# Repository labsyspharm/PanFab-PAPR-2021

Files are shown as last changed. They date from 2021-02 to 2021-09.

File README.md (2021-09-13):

# PanFab-PAPR-2021
Greater Boston Pandemic Fabrication Team Powered Air-Purifying Respirator (PanFab PAPR)

Akshay Kothakonda, Lyla Atta, Deborah Plana, Ferrous Ward, Nicole R. LeBoeuf, Peter K. Sorger, <i>et al </i>. 

Publication: https://www.frontiersin.org/articles/10.3389/fbioe.2021.690905/full

Website Intro Page Image-01

<br />This work is licensed under a <a rel="license" href="http://creativecommons.org/licenses/by-sa/4.0/">Creative Commons Attribution-ShareAlike 4.0 International License</a>.

Creative Commons License

This work is licensed under a Creative Commons Attribution-ShareAlike 4.0 International License.

Creative Commons Attribution-ShareAlike 4.0 International Public License

By exercising the Licensed Rights (defined below), You accept and agree to be bound by the terms and conditions of this Creative Commons Attribution-ShareAlike 4.0 International Public License ("Public License"). To the extent this Public License may be interpreted as a contract, You are granted the Licensed Rights in consideration of Your acceptance of these terms and conditions, and the Licensor grants You such rights in consideration of benefits the Licensor receives from making the Licensed Material available under these terms and conditions.

Section 1 – Definitions.

a.	Adapted Material means material subject to Copyright and Similar Rights that is derived from or based upon the Licensed Material and in which the Licensed Material is translated, altered, arranged, transformed, or otherwise modified in a manner requiring permission under the Copyright and Similar Rights held by the Licensor. For purposes of this Public License, where the Licensed Material is a musical work, performance, or sound recording, Adapted Material is always produced where the Licensed Material is synched in timed relation with a moving image.

b.	Adapter's License means the license You apply to Your Copyright and Similar Rights in Your contributions to Adapted Material in accordance with the terms and conditions of this Public License.

c.	BY-SA Compatible License means a license listed at creativecommons.org/compatiblelicenses, approved by Creative Commons as essentially the equivalent of this Public License.

d.	Copyright and Similar Rights means copyright and/or similar rights closely related to copyright including, without limitation, performance, broadcast, sound recording, and Sui Generis Database Rights, without regard to how the rights are labeled or categorized. For purposes of this Public License, the rights specified in Section 2(b)(1)-(2) are not Copyright and Similar Rights.

e.	Effective Technological Measures means those measures that, in the absence of proper authority, may not be circumvented under laws fulfilling obligations under Article 11 of the WIPO Copyright Treaty adopted on December 20, 1996, and/or similar international agreements.

f.	Exceptions and Limitations means fair use, fair dealing, and/or any other exception or limitation to Copyright and Similar Rights that applies to Your use of the Licensed Material.

g.	License Elements means the license attributes listed in the name of a Creative Commons Public License. The License Elements of this Public License are Attribution and ShareAlike.

h.	Licensed Material means the artistic or literary work, database, or other material to which the Licensor applied this Public License.

i.	Licensed Rights means the rights granted to You subject to the terms and conditions of this Public License, which are limited to all Copyright and Similar Rights that apply to Your use of the Licensed Material and that the Licensor has authority to license.

j.	Licensor means the individual(s) or entity(ies) granting rights under this Public License.

k.	Share means to provide material to the public by any means or process that requires permission under the Licensed Rights, such as reproduction, public display, public performance, distribution, dissemination, communication, or importation, and to make material available to the public including in ways that members of the public may access the material from a place and at a time individually chosen by them.

l.	Sui Generis Database Rights means rights other than copyright resulting from Directive 96/9/EC of the European Parliament and of the Council of 11 March 1996 on the legal protection of databases, as amended and/or succeeded, as well as other essentially equivalent rights anywhere in the world.

m.	You means the individual or entity exercising the Licensed Rights under this Public License. Your has a corresponding meaning.
Section 2 – Scope.

a.	License grant. 

1.	Subject to the terms and conditions of this Public License, the Licensor hereby grants You a worldwide, royalty-free, non-sublicensable, non-exclusive, irrevocable license to exercise the Licensed Rights in the Licensed Material to: 

A.	reproduce and Share the Licensed Material, in whole or in part; and

B.	produce, reproduce, and Share Adapted Material.

2.	Exceptions and Limitations. For the avoidance of doubt, where Exceptions and Limitations apply to Your use, this Public License does not apply, and You do not need to comply with its terms and conditions.

3.	Term. The term of this Public License is specified in Section 6(a).

4.	Media and formats; technical modifications allowed. The Licensor authorizes You to exercise the Licensed Rights in all media and formats whether now known or hereafter created, and to make technical modifications necessary to do so. The Licensor waives and/or agrees not to assert any right or authority to forbid You from making technical modifications necessary to exercise the Licensed Rights, including technical modifications necessary to circumvent Effective Technological Measures. For purposes of this Public License, simply making modifications authorized by this Section 2(a)(4) never produces Adapted Material.

5.	Downstream recipients. 

A.	Offer from the Licensor – Licensed Material. Every recipient of the Licensed Material automatically receives an offer from the Licensor to exercise the Licensed Rights under the terms and conditions of this Public License.

B.	Additional offer from the Licensor – Adapted Material. Every recipient of Adapted Material from You automatically receives an offer from the Licensor to exercise the Licensed Rights in the Adapted Material under the conditions of the Adapter’s License You apply.

C.	No downstream restrictions. You may not offer or impose any additional or different terms or conditions on, or apply any Effective Technological Measures to, the Licensed Material if doing so restricts exercise of the Licensed Rights by any recipient of the Licensed Material.

6.	No endorsement. Nothing in this Public License constitutes or may be construed as permission to assert or imply that You are, or that Your use of the Licensed Material is, connected with, or sponsored, endorsed, or granted official status by, the Licensor or others designated to receive attribution as provided in Section 3(a)(1)(A)(i).

b.	Other rights.

1.	Moral rights, such as the right of integrity, are not licensed under this Public License, nor are publicity, privacy, and/or other similar personality rights; however, to the extent possible, the Licensor waives and/or agrees not to assert any such rights held by the Licensor to the limited extent necessary to allow You to exercise the Licensed Rights, but not otherwise.

2.	Patent and trademark rights are not licensed under this Public License.

3.	To the extent possible, the Licensor waives any right to collect royalties from You for the exercise of the Licensed Rights, whether directly or through a collecting society under any voluntary or waivable statutory or compulsory licensing scheme. In all other cases the Licensor expressly reserves any right to collect such royalties.

Section 3 – License Conditions.

Your exercise of the Licensed Rights is expressly made subject to the following conditions.

a.	Attribution.

1.	If You Share the Licensed Material (including in modified form), You must:

A.	retain the following if it is supplied by the Licensor with the Licensed Material: 

i.	identification of the creator(s) of the Licensed Material and any others designated to receive attribution, in any reasonable manner requested by the Licensor (including by pseudonym if designated);

ii.	a copyright notice;

iii.	a notice that refers to this Public License; 

iv.	a notice that refers to the disclaimer of warranties;

v.	a URI or hyperlink to the Licensed Material to the extent reasonably practicable;

B.	indicate if You modified the Licensed Material and retain an indication of any previous modifications; and

C.	indicate the Licensed Material is licensed under this Public License, and include the text of, or the URI or hyperlink to, this Public License.

2.	You may satisfy the conditions in Section 3(a)(1) in any reasonable manner based on the medium, means, and context in which You Share the Licensed Material. For example, it may be reasonable to satisfy the conditions by providing a URI or hyperlink to a resource that includes the required information.

3.	If requested by the Licensor, You must remove any of the information required by Section 3(a)(1)(A) to the extent reasonably practicable.

b.	ShareAlike. 

In addition to the conditions in Section 3(a), if You Share Adapted Material You produce, the following conditions also apply.

1.	The Adapter’s License You apply must be a Creative Commons license with the same License Elements, this version or later, or a BY-SA Compatible License.

2.	You must include the text of, or the URI or hyperlink to, the Adapter's License You apply. You may satisfy this condition in any reasonable manner based on the medium, means, and context in which You Share Adapted Material.

3.	You may not offer or impose any additional or different terms or conditions on, or apply any Effective Technological Measures to, Adapted Material that restrict exercise of the rights granted under the Adapter's License You apply.

Section 4 – Sui Generis Database Rights.

Where the Licensed Rights include Sui Generis Database Rights that apply to Your use of the Licensed Material:

a.	for the avoidance of doubt, Section 2(a)(1) grants You the right to extract, reuse, reproduce, and Share all or a substantial portion of the contents of the database;

b.	if You include all or a substantial portion of the database contents in a database in which You have Sui Generis Database Rights, then the database in which You have Sui Generis Database Rights (but not its individual contents) is Adapted Material, including for purposes of Section 3(b); and

c.	You must comply with the conditions in Section 3(a) if You Share all or a substantial portion of the contents of the database.

For the avoidance of doubt, this Section 4 supplements and does not replace Your obligations under this Public License where the Licensed Rights include other Copyright and Similar Rights. 

Section 5 – Disclaimer of Warranties and Limitation of Liability.

a.	Unless otherwise separately undertaken by the Licensor, to the extent possible, the Licensor offers the Licensed Material as-is and as-available, and makes no representations or warranties of any kind concerning the Licensed Material, whether express, implied, statutory, or other. This includes, without limitation, warranties of title, merchantability, fitness for a particular purpose, non-infringement, absence of latent or other defects, accuracy, or the presence or absence of errors, whether or not known or discoverable. Where disclaimers of warranties are not allowed in full or in part, this disclaimer may not apply to You.

b.	To the extent possible, in no event will the Licensor be liable to You on any legal theory (including, without limitation, negligence) or otherwise for any direct, special, indirect, incidental, consequential, punitive, exemplary, or other losses, costs, expenses, or damages arising out of this Public License or use of the Licensed Material, even if the Licensor has been advised of the possibility of such losses, costs, expenses, or damages. Where a limitation of liability is not allowed in full or in part, this limitation may not apply to You.

c.	The disclaimer of warranties and limitation of liability provided above shall be interpreted in a manner that, to the extent possible, most closely approximates an absolute disclaimer and waiver of all liability.

Section 6 – Term and Termination.

a.	This Public License applies for the term of the Copyright and Similar Rights licensed here. However, if You fail to comply with this Public License, then Your rights under this Public License terminate automatically.

b.	Where Your right to use the Licensed Material has terminated under Section 6(a), it reinstates:

1.	automatically as of the date the violation is cured, provided it is cured within 30 days of Your discovery of the violation; or

2.	upon express reinstatement by the Licensor.

For the avoidance of doubt, this Section 6(b) does not affect any right the Licensor may have to seek remedies for Your violations of this Public License.

c.	For the avoidance of doubt, the Licensor may also offer the Licensed Material under separate terms or conditions or stop distributing the Licensed Material at any time; however, doing so will not terminate this Public License.

d.	Sections 1, 5, 6, 7, and 8 survive termination of this Public License.

Section 7 – Other Terms and Conditions.

a.	The Licensor shall not be bound by any additional or different terms or conditions communicated by You unless expressly agreed.

b.	Any arrangements, understandings, or agreements regarding the Licensed Material not stated herein are separate from and independent of the terms and conditions of this Public License.

Section 8 – Interpretation.

a.	For the avoidance of doubt, this Public License does not, and shall not be interpreted to, reduce, limit, restrict, or impose conditions on any use of the Licensed Material that could lawfully be made without permission under this Public License.

b.	To the extent possible, if any provision of this Public License is deemed unenforceable, it shall be automatically reformed to the minimum extent necessary to make it enforceable. If the provision cannot be reformed, it shall be severed from this Public License without affecting the enforceability of the remaining terms and conditions.

c.	No term or condition of this Public License will be waived and no failure to comply consented to unless expressly agreed to by the Licensor.

d.	Nothing in this Public License constitutes or may be interpreted as a limitation upon, or waiver of, any privileges and immunities that apply to the Licensor or You, including from the legal processes of any jurisdiction or authority.

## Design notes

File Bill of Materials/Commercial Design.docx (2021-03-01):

Bill of Materials for PanFab Commercial PAPR Design

Akshay Kothakonda¹ ,², *, Lyla Atta¹,³, *, Deborah Plana¹ ,⁴,⁵, *, Ferrous Ward¹ ,², *, Chris Davis¹,⁶, Avilash Cramer¹ ,⁵, Robert Moran¹ ,⁷, Jacob Freake¹,⁸, Enze Tian¹,⁹, Ofer Mazor¹,¹⁰, Pavel Gorelik¹,¹⁰, Christopher Van¹,¹¹, Christopher Hansen¹,¹², Helen Yang¹,¹³, Michael S. Sinha¹,¹³, Ju Li¹,¹⁴, Sherry H. Yu¹,¹⁵, Nicole R. LeBoeuf1,16, †, Peter K. Sorger1,4, †

¹ Greater Boston Pandemic Fabrication Team (PanFab) c/o Harvard-MIT Center for Regulatory Science, Harvard Medical School, Boston, MA, USA

²Department of Aeronautics and Astronautics, MIT, Cambridge, MA, USA

³Johns Hopkins University School of Medicine, Baltimore, MD, USA

⁴Harvard Ludwig Cancer Research Center and Department of Systems Biology, Harvard Medical School, Boston, MA, USA

⁵ Harvard-MIT Division of Health Sciences & Technology, Cambridge, MA, USA

⁶GenOne Technologies, Cambridge, MA, USA

⁷Mine Survival, Panama City Beach, FL, USA

⁸Fikst Product Development, Woburn, MA, USA

⁹Beijing Key Laboratory of Indoor Air Quality Evaluation and Control, Department of Building Science, Tsinghua University, Beijing, China

¹⁰Research Instrumentation Core Facility, Harvard Medical School, Boston, MA, USA

¹¹Borobot, Middleborough, MA, USA

¹²Harvard Graduate School of Design, Cambridge, MA, USA

¹³Harvard-MIT Center for Regulatory Science, Harvard Medical School, Boston MA, USA

¹⁴Department of Nuclear Science and Engineering and Department of Materials Science and Engineering, MIT, Cambridge, MA, USA

¹⁵Department of Dermatology, Yale School of Medicine, New Haven, CT USA

¹⁶ Department of Dermatology, Center for Cutaneous Oncology, Brigham and Women’s Hospital and Dana-Farber Cancer Institute, Boston, MA, USA

*These authors contributed equally to this work

†Co-corresponding authors. E-mails: nleboeuf@bwh.harvard.edu; peter_sorger@hms.harvard.edu cc: Maureen_Bergeron@hms.harvard.edu;

ORCID IDs:

Akshay Kothakonda, 0000-0001-5424-4228

Lyla Atta, 0000-0002-6113-0082

Deborah Plana, 0000-0002-4218-1693

Avilash Cramer, 0000-0003-0014-8921

Jacob Freake, 0000-0002-5198-835X

Enze Tian, 0000-0001-6410-5360

Christopher Van, 0000-0003-3262-964X

Christopher Hansen, 0000-0002-6640-2745

Ju Li, PhD, 0000-0002-7841-8058

Helen Yang, 0000-0002-9455-5300

Michael S. Sinha 0000-0002-9165-8611

Sherry H. Yu: 0000-0002-1432-9128

Nicole R. LeBoeuf, MD, MPH, 0000-0002-8264-834X

Peter Sorger, PhD, 0000-0002-3364-1838

Following are the parts used in the PanFab Commercial PAPR Design. The estimated costs assume a total production run of 2000 units.

S. No. | Item | Qty. | Supplier/Method | Part No. | Estimated cost ($)
1 | Enclosure | 1 | Pelican | V100 Vault | 40
2 | Threaded Inserts for Filter | 2 | ABS Molding | N/A | 6 (Tooling Cost = 6645)
3 | Threaded Insert for Hose | 1 | ABS Molding | N/A | 2.80 (Tooling Cost = 6846)
4 | Blower, Centrifugal | 1 | Delta Electronics | BFB1012HD-04D4L | 36
5 | Battery pack, 12V NiMH | 1 | Tenergy | Amazon Standard Identification Number: B077Y9HNTF | 23
6 | Controller | 1 | Arduino | R3 | 23
7 | PCB Shield | 1 | OSH Park | N/A | 9.50
8 | Differential Pressure Sensor | 1 | Sensirion | SDP810-500PA | 19
9 | Buzzer | 1 | Mallory Sonalert Products | PS-580Q | 5
10 | Potentiometer | 1 | Bourns Inc. | 93R1A-R22-A12L | 3
11 | Transistor | 1 | ON Semiconductor | 2N3904BU | 0.20
12 | Resistor | 1 | Vishay BC Semiconductor | PR02000201001JR500 | 0.32
13 | Electrical connector | 1 | TE Connectivity AMP Connectors | 1-2834184-3 | 1.40
14 | Venturi | 1 | BPE Inc. | 178-71-2 | 0.54
15 | Venturi Ports | 2 | Car-Anth Manufacturing | 16-1204-2 | 0.68 (Tooling Cost = 375)
16 | Blower silicone tube | 1 | McMaster-Carr | 3038K29 | N/A
17 | Venturi silicone tube | 2 | McMaster-Carr | 3038K12 | N/A
18 | Blower adapter | 1 | ABS 3D printing | N/A | 6
20 | Switch | 1 | McMaster-Carr | 8002K114 | 28
21 | Switch Cover | 1 | McMaster-Carr | 70205K4 | 4.40
22 | Gaskets for threaded connections | 4 | McMaster-Carr | 5647K62 | 3
23 | Waist strap | 1 | Skil-Care | PathoShield Gait Belt | 11
24 | Filter | 2 | Milwaukee | 49-90-1900 | 40
25 | Filter Adapter | 2 | ABS Injection molding | N/A | 6 (Tooling Cost = 6846)
26 | Filter Cover | 2 | ABS Injection molding | N/A | 8 (Tooling Cost = 18345)
27 | Hose adapter | 2 | ABS Injection molding | N/A | 6.60 (Tooling Cost = 9997)
28 | Hose | 1 | Flexaust | Flex-Tube PU-IH, PN: 33800125000 | 8.50
29 | Hood coupler | 1 | ABS Injection molding | N/A | 3.30 (Tooling Cost = 7456)
30 | Locking ring | 1 | ABS Injection molding | N/A | 2.70 (Tooling Cost = 5156)
31 | Hood | 1 | University of Washington | VHA ADAPT PAPR Hood | 30
Total | | | | | 327.94

Notes:

1. Several costs are unofficial quotes

2. Tooling cost for machining the Pelican case and joining the threaded inserts (Items 2 and 3) are TBD

© President and Fellows of Harvard College and The Massachusetts Institute of Technology, 2020.

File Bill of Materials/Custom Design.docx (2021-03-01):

Bill of Materials for PanFab Custom PAPR Design

Akshay Kothakonda¹ ,², *, Lyla Atta¹,³, *, Deborah Plana¹ ,⁴,⁵, *, Ferrous Ward¹ ,², *, Chris Davis¹,⁶, Avilash Cramer¹ ,⁵, Robert Moran¹ ,⁷, Jacob Freake¹,⁸, Enze Tian¹,⁹, Ofer Mazor¹,¹⁰, Pavel Gorelik¹,¹⁰, Christopher Van¹,¹¹, Christopher Hansen¹,¹², Helen Yang¹,¹³, Michael S. Sinha¹,¹³, Ju Li¹,¹⁴, Sherry H. Yu¹,¹⁵, Nicole R. LeBoeuf1,16, †, Peter K. Sorger1,4, †

¹ Greater Boston Pandemic Fabrication Team (PanFab) c/o Harvard-MIT Center for Regulatory Science, Harvard Medical School, Boston, MA, USA

²Department of Aeronautics and Astronautics, MIT, Cambridge, MA, USA

³Johns Hopkins University School of Medicine, Baltimore, MD, USA

⁴Harvard Ludwig Cancer Research Center and Department of Systems Biology, Harvard Medical School, Boston, MA, USA

⁵ Harvard-MIT Division of Health Sciences & Technology, Cambridge, MA, USA

⁶GenOne Technologies, Cambridge, MA, USA

⁷Mine Survival, Panama City Beach, FL, USA

⁸Fikst Product Development, Woburn, MA, USA

⁹Beijing Key Laboratory of Indoor Air Quality Evaluation and Control, Department of Building Science, Tsinghua University, Beijing, China

¹⁰Research Instrumentation Core Facility, Harvard Medical School, Boston, MA, USA

¹¹Borobot, Middleborough, MA, USA

¹²Harvard Graduate School of Design, Cambridge, MA, USA

¹³Harvard-MIT Center for Regulatory Science, Harvard Medical School, Boston MA, USA

¹⁴Department of Nuclear Science and Engineering and Department of Materials Science and Engineering, MIT, Cambridge, MA, USA

¹⁵Department of Dermatology, Yale School of Medicine, New Haven, CT USA

¹⁶ Department of Dermatology, Center for Cutaneous Oncology, Brigham and Women’s Hospital and Dana-Farber Cancer Institute, Boston, MA, USA

*These authors contributed equally to this work

†Co-corresponding authors. E-mails: nleboeuf@bwh.harvard.edu; peter_sorger@hms.harvard.edu cc: Maureen_Bergeron@hms.harvard.edu;

ORCID IDs:

Akshay Kothakonda, 0000-0001-5424-4228

Lyla Atta, 0000-0002-6113-0082

Deborah Plana, 0000-0002-4218-1693

Avilash Cramer, 0000-0003-0014-8921

Jacob Freake, 0000-0002-5198-835X

Enze Tian, 0000-0001-6410-5360

Christopher Van, 0000-0003-3262-964X

Christopher Hansen, 0000-0002-6640-2745

Ju Li, PhD, 0000-0002-7841-8058

Helen Yang, 0000-0002-9455-5300

Michael S. Sinha 0000-0002-9165-8611

Sherry H. Yu: 0000-0002-1432-9128

Nicole R. LeBoeuf, MD, MPH, 0000-0002-8264-834X

Peter Sorger, PhD, 0000-0002-3364-1838

Following are the parts used in the PanFab Custom PAPR Design. The estimated costs assume a total production run of 2000 units.

S. No. | Item | Qty. | Supplier/Method | Part No. | Estimated cost ($)
1 | Housing Bin | 1 | ABS Injection Molding | N/A | 9.60 (Tooling Cost = 10,720)
2 | Housing Lid | 1 | ABS Injection Molding | N/A | 9.70 (Tooling Cost = 19,589)
3 | Blower, Centrifugal | 1 | Delta Electronics | BFB1012HD-04D4L | 36
4 | Battery pack, 12V NiMH | 1 | Tenergy | Amazon Standard Identification Number: B077Y9HNTF | 23
5 | Controller | 1 | Arduino | R3 | 23
6 | PCB Shield | 1 | OSH Park | N/A | 9.50
7 | Differential Pressure Sensor | 1 | Sensirion | SDP810-500PA | 19
8 | Buzzer | 1 | Mallory Sonalert Products | PS-580Q | 5
9 | Potentiometer | 1 | Bourns Inc. | 93R1A-R22-A12L | 3
10 | Transistor | 1 | ON Semiconductor | 2N3904BU | 0.20
11 | Resistor | 1 | Vishay BC Semiconductor | PR02000201001JR500 | 0.32
12 | Electrical connector | 1 | TE Connectivity AMP Connectors | 1-2834184-3 | 1.40
13 | Venturi | 1 | BPE Inc. | 178-71-2 | 0.54
14 | Venturi Ports | 2 | Car-Anth Manufacturing | 16-1204-2 | 0.68 (Tooling Cost = 375)
15 | Blower silicone tube | 1 | McMaster-Carr | 3038K29 | N/A
16 | Venturi silicone tube | 2 | McMaster-Carr | 3038K12 | N/A
17 | Blower adapter | 1 | ABS 3D printing | N/A | 6
18 | Housing Gasket | 1 | Apple Rubber | N/A | 3.20 (Tooling Cost = 2560)
19 | Housing Latches | 4 | McMaster-Carr | 1794A55 | 15.20
20 | Gaskets for threaded connections | 4 | McMaster-Carr | 5647K62 | 3
21 | Latch screws | 16 | McMaster-Carr | 98164A441 | 1.55
22 | Latch nuts | 16 | McMaster-Carr | 90730A007 | 0.65
23 | Switch | 1 | McMaster-Carr | 8002K114 | 28
24 | Switch Cover | 1 | McMaster-Carr | 70205K4 | 4.40
25 | Waist strap | 1 | Skil-Care | PathoShield Gait Belt | 11
26 | Filter | 2 | Custom Filters | N/A | 19 (Tooling Cost = 26020)
27 | Hose adapter | 2 | ABS Injection molding | N/A | 6.60 (Tooling Cost = 9997)
28 | Hose | 1 | Flexaust | Flex-Tube PU-IH, PN: 33800125000 | 8.50
29 | Hood coupler | 1 | ABS Injection molding | N/A | 3.30 (Tooling Cost = 7456)
30 | Locking ring | 1 | ABS Injection molding | N/A | 2.70 (Tooling Cost = 5156)
31 | Hood | 1 | University of Washington | VHA ADAPT PAPR Hood | 30
Total | | | | | 284.04

Note: Several costs are unofficial quotes

© President and Fellows of Harvard College and The Massachusetts Institute of Technology, 2020.

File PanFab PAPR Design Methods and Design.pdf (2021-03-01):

© President and Fellows of Harvard College and The Massachusetts Institute of Technology,

PanFab PAPR Design Methods and Design
Akshay Kothakonda¹ ,2, *, Lyla Atta¹,3, *, Deborah Plana¹ ,4,5, *, Ferrous Ward¹ ,2, *, Chris Davis¹,6, Avilash Cramer¹ ,5, Robert Moran¹ ,7, Jacob Freake¹,8, Enze Tian¹,9, Ofer Mazor¹,10, Pavel Gorelik¹,10, Christopher Van¹,11, Christopher Hansen¹,12, Helen Yang¹,13, Michael S. Sinha¹,13, Ju Li¹,14, Sherry H. Yu¹,15, Nicole R. LeBoeuf¹,16, †, Peter K. Sorger¹,4, †
1 Greater Boston Pandemic Fabrication Team (PanFab) c/o Harvard-MIT Center for Regulatory Science, Harvard Medical School, Boston, MA, USA
2
Department of Aeronautics and Astronautics, MIT, Cambridge, MA, USA
3
Johns Hopkins University School of Medicine, Baltimore, MD, USA
4
Harvard Ludwig Cancer Research Center and Department of Systems Biology, Harvard Medical School, Boston, MA, USA
5 Harvard-MIT Division of Health Sciences & Technology, Cambridge, MA, USA
6
GenOne Technologies, Cambridge, MA, USA
7
Mine Survival, Panama City Beach, FL, USA
8
Fikst Product Development, Woburn, MA, USA
9
Beijing Key Laboratory of Indoor Air Quality Evaluation and Control, Department of Building Science, Tsinghua University, Beijing, China
10Research Instrumentation Core Facility, Harvard Medical School, Boston, MA, USA 11Borobot, Middleborough, MA, USA
12Harvard Graduate School of Design, Cambridge, MA, USA
13Harvard-MIT Center for Regulatory Science, Harvard Medical School, Boston MA, USA 14Department of Nuclear Science and Engineering and Department of Materials Science and Engineering, MIT, Cambridge, MA, USA
15Department of Dermatology, Yale School of Medicine, New Haven, CT USA
16 Department of Dermatology, Center for Cutaneous Oncology, Brigham and Women’s Hospital and Dana-Farber Cancer Institute, Boston, MA, USA

*
These authors contributed equally to this work
†
Co-corresponding authors. E-mails: nleboeuf@bwh.harvard.edu; peter_sorger@hms.harvard.edu cc: Maureen_Bergeron@hms.harvard.edu;

ORCID IDs:
Akshay Kothakonda, 0000-0001-5424-4228
Lyla Atta, 0000-0002-6113-0082
Deborah Plana, 0000-0002-4218-1693 Avilash Cramer, 0000-0003-0014-8921 Jacob Freake, 0000-0002-5198-835X Enze Tian, 0000-0001-6410-5360 Christopher Van, 0000-0003-3262-964X Christopher Hansen, 0000-0002-6640-2745 Ju Li, PhD, 0000-0002-7841-8058

© President and Fellows of Harvard College and The Massachusetts Institute of Technology,

Helen Yang, 0000-0002-9455-5300
Michael S. Sinha 0000-0002-9165-8611
Sherry H. Yu: 0000-0002-1432-9128
Nicole R. LeBoeuf, MD, MPH, 0000-0002-8264-834X Peter Sorger, PhD, 0000-0002-3364-1838

METHODS
This section describes the methodology pursued in designing the PanFab Custom PAPR and PanFab Commercial PAPR filters and blower units.
Filter selection
NIOSH regulations designate several classes of PAPRs depending on filtration requirements. A key distinction between classes is whether the respirator is approved for use with oil-based aerosols (P type filters, tested for filtration efficiency with dioctyl phthalate (DOP)) or only aqueous aerosols (N type filters, tested for filtration efficiency with NaCl-containing droplets). Commercial PAPR filter cartridges are commonly of the P100 type as they provide protection against both oil and salt-based aqueous aerosols. Another, less commonly used, class of PAPR filter is the N100, which only needs to demonstrate its effectiveness against salt-based aqueous aerosols and not oil. Here, “100” after the type designation refers to filters demonstrating filtration of 99.97% of tested particles¹.
The pressure drop across a filter at the required airflow is an additional consideration that affects blower selection and power consumption. The pressure drop should be as low as possible for a given filtration efficiency, so as to permit the use of a less powerful blower, and consequently a smaller battery, making the system lighter and able to operate longer between charging².

© President and Fellows of Harvard College and The Massachusetts Institute of Technology,

In selecting the PanFab Commercial Filter Cartridge, our goal was to identify and test commercially available products whose supply would not be impacted by shortages during pandemic conditions, and which would be easily adaptable to various blower units. The PanFab Custom Filter Cartridge was designed to have a small overall volume, be lightweight, and have integrated connection features to allow for compatibility with various blower units.

Blower Unit Design

The PAPR blower units consist of a blower, battery, buzzer to warn of low flow rate, control systems, and a housing to enclose these components. The PanFab commercial and custom units were designed to be comfortable to wear for extended periods of time, to be easy to don and doff, and to not hamper the range of motion required in clinical tasks. Additionally, the materials for the external surfaces of the unit were selected so as to be compatible with sterilization with alcohol based wipes. Below we outline the selection criteria used for each of the blower unit components.
The PanFab blowers were selected to produce enough static pressure as to overcome the pressure drop incurred from passing air through the filters and the facepiece at the required flow rate of 170 liters per minute³. The commercial and custom battery that powers the blower unit were selected to match the voltage rating of the blower and have sufficient discharge current. We also ensured the batteries had the charge capacity necessary to continuously power the blower for one hour or longer at the required flow rate, a time selected based on the recommendations from HCWs at a major academic medical center. Finally, we ensured that the blower and battery combinations met the NIOSH specification for a noise level at the user’s ears below 80 dBA³. The blower unit control system was designed to measure the air flow rate through the PAPR and to sound an alarm at a sound level above 80 dBA at the ears (as per NIOSH STP

© President and Fellows of Harvard College and The Massachusetts Institute of Technology,

CVB-APR-STP-008) to alert the wearer of a low flow condition. The control system was also designed so as to allow for modulating flow rate as needed by the wearer.
The blower unit housings were selected to couple and decouple with the filters and hose by hand without requiring specialized tools, and to be conducive to frequent opening and closing for operations including battery charging, flow rate adjustment, and troubleshooting. Since the air inside the housing has been filtered and there is negative pressure inside the housing, it is essential for the connections of the housing with the filters and the hose, as well the interface between the separable sections of the housing, to be airtight.
Facepiece selection
We used a loose-fitting facepiece, known as the VHA ADAPT PAPR Hood, developed by the The Center for Limb Loss and MoBility (CLiMB) at the University of Washington⁴. This low cost facepiece was developed as part of COVID-19 response efforts and was chosen for prototype testing as commercial facepieces were not readily available.

RESULTING DESIGNS
This section details the designs that resulted for both the PanFab Custom PAPR and the PanFab Commercial PAPR filter and blower units.

PanFab filter cartridges
PanFab Commercial Filter Cartridge
We investigated commercial High Efficiency Particulate Air (HEPA) filters commonly used in vacuum cleaners as possible candidates. HEPA filters are rated as 99.97% efficient at

© President and Fellows of Harvard College and The Massachusetts Institute of Technology,

300um particle size⁵. The cost and availability of the Milwaukee Tool (Brookfield, WI)⁶ in commercial stores was particularly well suited to the crisis-setting PanFab PAPR design.
In order to connect the Milwaukee filter to the housings, an adapter was designed, which could be either 3D printed or injection molded. This adapter would be sealed to the filter outlet on one side using sealants or adhesives such as cyanoacrylate or epoxies, and on the other side would connect to the housing using male NATO 40mm threads. Filter covers were also designed for these filter cartridges, that protect the filter sheet from damage. These covers are also designed to be printed or molded.

PanFab Custom Filter Cartridge
We also designed a custom filter cartridge in collaboration with Custom Filters LLC (Aurora, IL) to decrease the weight and size of these devices as compared to the Milwaukee filters, making them more comfortable and easier to use for prolonged periods of time in healthcare settings. These cartridges do not need a separate filter cover, since the cartridge body is designed to envelop the filter media. Additionally, Custom Filters tests every filter cartridges’ instantaneous filtration efficiency with PAO aerosol, ensuring the integrity of all filters. This filter also connects to the housing through integrated male NATO 40mm threads.

PanFab blower units
We designed the PanFab Commercial and Custom blower units to have the same internal components, with different housings enclosing the components. NIOSH guidelines specify that airflow into a loose-fitting facepiece must exceed 170 liters/minute (lpm) to ensure maintenance of positive pressure at all activity levels ⁷. We chose to design our PAPR to provide 230 lpm,

© President and Fellows of Harvard College and The Massachusetts Institute of Technology, similar to some of the commercial PAPR’s. In selecting a blower, we determined that compact centrifugal blowers (compared to axial fans) could provide the necessary static pressures needed to overcome the pressure drop created by the filter at the required flow rate, as well as to overcome losses over the flow path to the facepiece. The pressure drop across the filters at the required flow rate was determined as part of the filtration efficiency tests. The blower selected (Delta Electronics, Neihu, Taiwan, Part Number BFB1012HD-04D4L) has a maximum static pressure of 40.6 mm of H2O and a maximum flow rate of 18.3 cubic feet per meter (cfm). Additionally, the noise level generated by running the PAPR should not exceed 80 dBA per NIOSH guidelines and should allow for sufficient communication between users⁸. The blower selected has a maximum noise level rated at 50.5dBA at a distance of 1 m. In order to meet the requirements of the blower, a 12V NiMH battery pack (Tenergy, Fremont, CA, Amazon Standard Identification Number: B077Y9HNTF) was selected. The battery has a charge capacity of 2000mA, which provides almost 4 hours of continuous operation, at the maximum flow rate, which is higher than the 1hour requirement. The battery connects to the switch through a manual disconnect, which can be disconnected to connect to a Tenergy battery charger (Amazon Standard Identification Number: B08J4H39JV).
The control system of the PAPR consists of an Arduino Uno R3 (Arduino LLC, Boston, MA) board, a linear potentiometer (Precision Electronics Corporation, North York, ON, Canada, part number RV4NAYSD103A) which controls the duty cycle, and consequently the speed of the blower, a printed circuit board (PCB)-mounted, I2C protocol operated differential pressure sensor (Sensirion AG, Staefa, Switzerland, part number SDP810-500PA) which estimates the flow rate, a piezoelectric buzzer (Mallory Sonalert Products Inc., Indianapolis, IN, part number PS-580Q) which warns of low flow rate, and a manual SPST switch (purchased from McMaster-

© President and Fellows of Harvard College and The Massachusetts Institute of Technology,

Carr, Elmhurst, IL, part number 8002K114) to turn on and off the device. A custom shield was designed and printed at OSH Park (Portland, OR), which assembles with the Arduino, and solders to the various components. An Arduino Protoshield can also be used in place of the custom printed shield.
NIOSH requires PAPRs to have a low flow rate alarm that is activated when airflow into the facepiece falls below the threshold of 170 lpm, which in our design is activated below 230 lpm. In the PanFab PAPR design, the differential pressure sensor detects pressure differential across a venturi (provided by Hunter Engineering Company, Bridgeton, MO), connected to the outlet of the blower, via a 3D printed blower adapter and a 1” OD Silicone tube (purchased from McMaster-Carr, part number 3038K29). Ports of the venturi are connected to the corresponding ones on the differential pressure sensor through a 7/32” OD Silicone tube (purchased from McMaster-Carr, part number 3038K12). It should be noted that the blower adapter connecting the blower outlet to the 1” Silicone tube was designed specifically for the blower selected; a different blower would require a blower adapter design compliant with its outlet geometry. In order to calibrate the threshold differential pressure corresponding to the threshold flow rate of 230 lpm, the outlet of the venturi was first connected to the Vernier anemometer. The differential pressure sensor was connected to an Arduino Uno R3 board through a custom printed shield, compatible with the Arduino board. The differential pressure across the venturi is read on the Arduino Serial Monitor User Interface, which is plotted against the air speed as the blower speed is increased. The minimum flow rate of 230 lpm is now correlated to the corresponding differential pressure. Once this calibration is done, the differential pressure value obtained is used in microcontroller logic to sound a piezoelectric buzzer, when the differential pressure falls below this value (and the corresponding flow rate) for 10 consecutive seconds. The

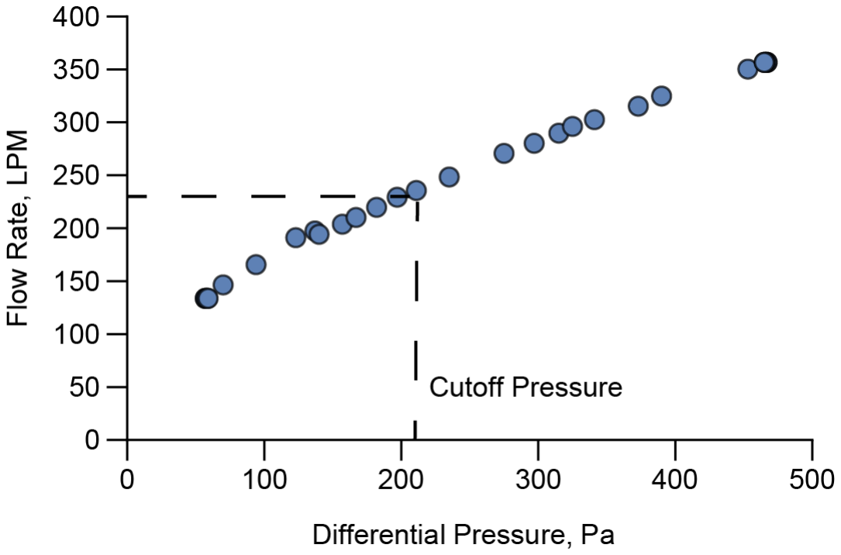
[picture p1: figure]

© President and Fellows of Harvard College and The Massachusetts Institute of Technology, plot of flow rate vs. differential pressure measured, with observed datapoints is shown in Figure 1 below. The cutoff pressure corresponding to the cutoff flow rate of 230 lpm is marked, which was programmed in the Arduino.

Figure 1: Calibration of flow rate through the venturi to the pressure differential across the device, allowing identification of cutoff pressure corresponding to the cutoff flow rate of 230 LPM. Below this cutoff pressure, the piezoelectric buzzer is programmed to sound, alerting the wearer of low flow.
The sound level of the piezoelectric buzzer needs to be loud enough so as to sufficiently alert the wearer of a low flow condition. NIOSH requires the alarm to have a sound level above 80dBA at the ears. We chose a buzzer with a higher sound level since the buzzer is placed inside the housing. Unobstructed, the buzzer chosen is specified as producing 100 dB at a distance of 100 cm.

© President and Fellows of Harvard College and The Massachusetts Institute of Technology,

In order to maximize the sound level at the ears, the piezoelectric buzzer, installed inside the housing, with filters, hose, and facepiece connected, was programmed to sound at various frequencies. The frequency producing the maximum sound level at the ears was selected, which was done for both housing types, given the different sound attenuating properties expected from the two housings. For the custom housing that will be discussed later, the frequency obtained was 500 Hz, while for the commercial housing, it was 1500 Hz.
In order to simplify the control electronic design and code, a compensatory logic that would automatically increase the flow rate in the event of flow obstruction was considered but not adopted. Based on clinical feedback, very few scenarios were known to exist in clinical procedures where flow obstruction through a PAPR would be of concern. Nevertheless, the user can increase or decrease the flow rate to a comfortable level using the potentiometer, as long as it is above the threshold of 230 lpm.
All the components inside the blower unit is shown in Figure 2A and the circuit diagram of the control system is shown in Figure 2B.

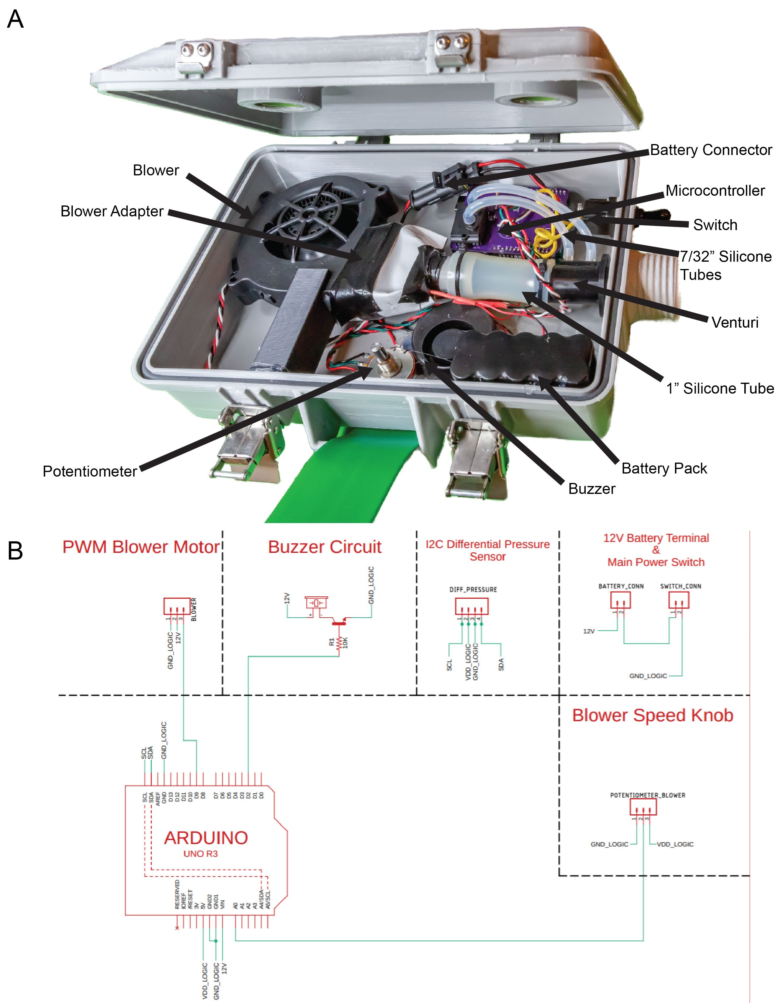
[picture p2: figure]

© President and Fellows of Harvard College and The Massachusetts Institute of Technology,

© President and Fellows of Harvard College and The Massachusetts Institute of Technology,

Figure 2: PanFab blower unit. A) Components inside the PAPR blower unit. B) Circuit diagram of the blower unit components.

The housing for the components of the blower units requires an airtight seal and needs to be compatible with the filter cartridge connectors and the facepiece hose connector. We designed two housings, the PanFab Commercial Design blower unit housing uses a commercially available container, modified to connect to the filter cartridges and the facepiece hose, and the PanFab Custom Design blower unit housing is fabricated entirely using 3D-printing or injection molding methods. Both housings are compatible with both of the PanFab-designed filter cartridges, as well as ILC Dover (Frederica, DE) filter cartridges via 40mm NATO threaded connections.

PanFab Custom blower units housing
The blower, battery, and all the electronics were enclosed in a custom housing made of PET-G designed for 3D printing and also optimized for injection molding. 3D printing is advantageous in this setting because it is widely available and compatible with low-volume production; injection molding requires a relatively expensive mold but has the advantage of lower unit cost and rapid production for higher volume production. The housing was printed using Fused Deposition Modeling (FDM) printing, on a RailCore II 300ZLT 3D printer. Layer height of 300 micron was used with 15% rectilinear infill and with 4 vertical shells. Integrated industry-standard female NATO 40 mm threaded connections enable attachment of the two filter cartridges and a male NATO 40 mm threaded connection enables attachment of a thermoplastic polyurethane hose to the housing while maintaining an airtight seal. Custom adapters were designed to attach hose to the NATO threaded outlet on one end and to the facepiece on the other

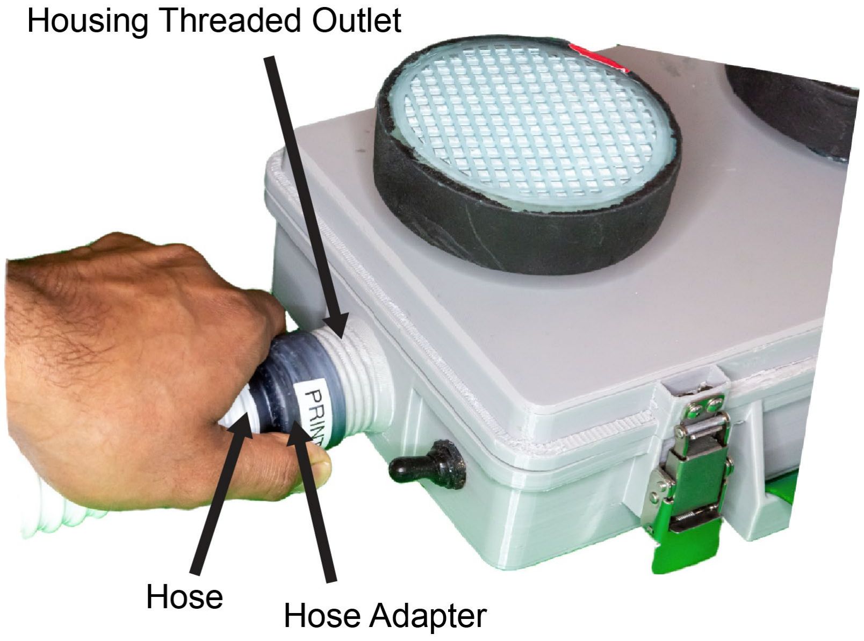
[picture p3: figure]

© President and Fellows of Harvard College and The Massachusetts Institute of Technology, end. The hose adapters are threaded into the hose to form a tight, interference fit. All NATO 40mm female connection features incorporate a gasket seat, which accommodates an ethylene propylene diene monomer (EPDM) 1/4” cam-and-groove gasket (purchased from McMaster-Carr, part number 5647K62). Figure 3 below shows the connection of the hose to the housing outlet, through the hose adapter.

Figure 3: Hose connection to PanFab blower unit outlet.
The housing is made of two detachable parts- a “lid” that closes over a “bin” and is locked with 4 draw latches (purchased from McMaster-Carr, part number 1794A55). The bin has a groove feature along its perimeter to accommodate a 1/8” silicone O-ring. The lid has a tongue profile that fits inside the groove and compresses the O-ring, providing sealing. In our prototypes, we used O-ring cord stock (purchased from McMaster-Carr, part number 5229T51), which was cut to size and glued at ends with silicone-based adhesive. For production parts, O-

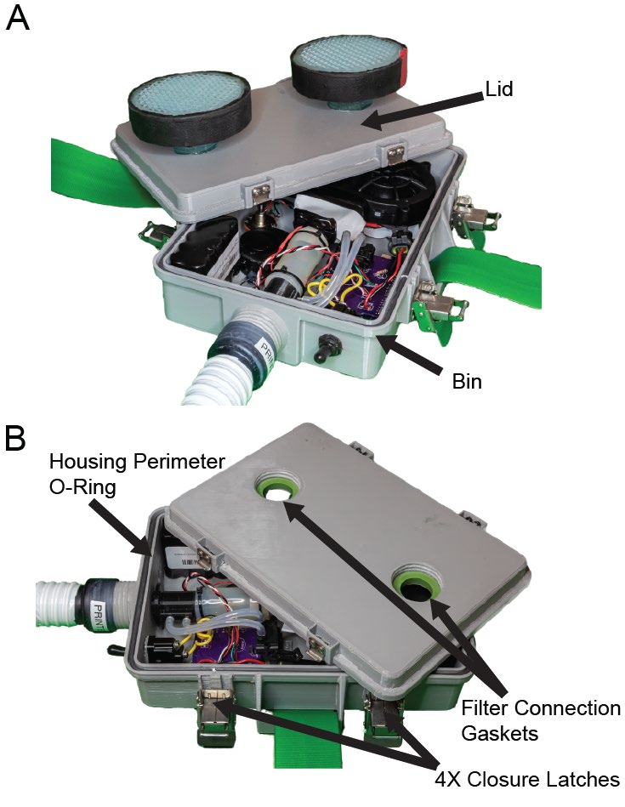
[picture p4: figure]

© President and Fellows of Harvard College and The Massachusetts Institute of Technology, rings of the required diameter (according to total perimeter of the groove, as per CAD models in Supplementary Material 4) can be molded. Figures 4A and 4B below shows the parts of the housing and the sealing features respectively.

Figure 4: PanFab blower unit. A) Custom blower unit housing and B) sealing features. The housing is printed with a hole to accommodate a MIL-spec power switch which connects/disconnects the battery pack to the rest of the circuit. Sealing between the switch and

© President and Fellows of Harvard College and The Massachusetts Institute of Technology, the housing is achieved by screwing a switch cover (purchased from McMaster-Carr, part number 70205K4) over the switch toggle. The base of the cover forms a seal with the housing surface upon tightening, which is kept from loosening by applying Loctite Threadlocker Red 271 (Loctite, Hartford, CT) on the threads during the cover installation.
A waist belt, designated as PathoShield Gait Belt, purchased from Skil-Care (Yonkers, NY) is run through two integrated loops in the bin part of the housing, which allows donning the blower unit on the lower back position. The belt is specifically manufactured to be amenable to sterilization.
CAD files for the housing are available in Supplementary Material 4.

PanFab Commercial blower unit housing
Since some groups may not have ready access to sufficiently large 3D printers, we have also adapted a commercially molded plastic case, the Pelican V100 Vault Small Pistol Case (Pelican products, Torrance, CA). Four holes of different sizes are made in this case, two of which accommodate and seal with two filter connection inserts, one accommodates and seals with a hose insert, and one with the power switch. These custom designed inserts are also compatible with both 3D printing and injection molding. These inserts enable connecting the housing to the filter and hose through the NATO 40mm threaded connectors, as in the case of the custom housing. The switch is also installed and sealed in a similar way. The inserts would be plastic welded onto the Pelican case, however in our prototypes, we used cyanoacrylate to seal the inserts to the case. The Pelican case comes with a pre-installed perimeter gasket, which provides the required sealing. Finally, the as-bought case also has an equalization valve, which in

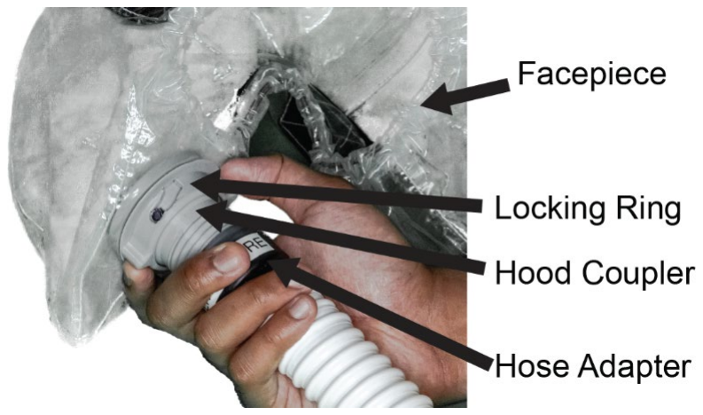
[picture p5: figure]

© President and Fellows of Harvard College and The Massachusetts Institute of Technology, its normal use prevents buildup of moisture inside the case, which is sealed off first using cyanoacrylate, and then hot melt glue over it, for its use as a PAPR.
Two loops of the Skil-Care belts are separately printed or molded and then welded (glued with cyanoacrylate in the prototype) to the case.

Facepiece integration
We used our prototypes with the loose-fitting UW VHA ADAPT PAPR Hood. The facepiece has a circular hole at the back of the head, to allow for connection with the hose. The hose adapter on the facepiece side was screwed over a hollow hood coupler, which passes through the hole in the facepiece. A tight connection between the facepiece material and the hood coupler was achieved by engaging a locking ring, which has a locking feature and locks with the hood coupler upon twisting, pressing the facepiece between them. Figure 5 below shows this connection. The PAPR designs discussed in this paper are also compatible with other facepieces with the NATO 40 mm threaded connection. Furthermore, the design of the hood coupler can be modified as needed, to make it compatible with any other facepiece.

Figure 5: Connection of the hose with facepiece, through hose adapter, hood coupler, and locking ring.

© President and Fellows of Harvard College and The Massachusetts Institute of Technology,

REFERENCES

1. Stafford, R. G. & Ettinger, H. J. Filter efficiency as a function of particle size and velocity. Atmospheric Environ. 1967 6, 353–362 (1972).
2. Zhu, J. et al. A pilot study of minimum operational flow for loose-fitting powered air-purifying respirators used in healthcare cleaning services. J. Occup. Environ. Hyg. 16, 440–445 (2019).
3. Approval Tests and Standards for Air-Purifying Particulate Respirators. Federal Register https://www.federalregister.gov/documents/2020/04/14/2020-07804/approval-tests-and-standards-for-air-purifying-particulate-respirators (2020).
4. Research centers. Mechanical Engineering https://www.me.washington.edu/research/centers (2012).
5. EPA. What is a HEPA filter? https://www.epa.gov/indoor-air-quality-iaq/what-hepa-filter-1 (2019).
6. HEPA Filter. https://www.milwaukeetool.com/Products-Repository/North-America/Accessories/Miscellaneous/Vacuum-Accessories/49-90-1900.
7. The Use and Effectiveness of Powered Air Purifying Respirators in Health Care: Workshop Summary. 18990 (National Academies Press, 2015). doi:10.17226/18990.
8. Current Standard Testing Procedures for Air-Purifying Respirators | NPPTL | NIOSH | CDC.
https://www.cdc.gov/niosh/npptl/stps/apresp.html (2020).

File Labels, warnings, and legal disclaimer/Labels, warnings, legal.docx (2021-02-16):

# Labels and Warnings

## Appropriate Use Criteria

This supplementary Powered Air Purifying Respirator (PAPR) was created as an emergency action in effort to protect people by providing backup Personal Protective Equipment (PPE) options if the standard PPE has become unavailable. This device has not gone through the same regulatory approval process as standard PPE but has gone through a special verification process expedited strictly for the response to the COVID-19 pandemic. The use of this supplementary PAPR should always come secondary to existing PPE equipment, standards, and protocol options if available. The decision to implement this device should be made with careful consideration and under the consultation of the corresponding institution’s occupational health and infection control departments.

The information included in this document provides a best-effort protocol to minimize the risk of viral transmission during assembly and delivery, as well as produce PAPRs whose quality is as consistent as possible.

## LEGAL DISCLAIMER

THIS PAPR DESIGN AND SPECIFICATIONS (THE “DESIGN”) IS PROVIDED “AS IS” AND PANFAB IS NOT RESPONSIBLE FOR ENSURING THAT ONE’S USE OF THE DESIGN WILL BE CLINICALLY SOUND, WITHOUT ERROR, OR OTHERWISE SUCCESSFUL. THE DESIGN HAS NOT BEEN TESTED OR APPROVED FOR USE IN A HEALTHCARE SETTING AND THE DESIGN IS NOT APPROVED BY ANY REGULATORY BODY. IF YOU CHOOSE TO USE THE DESIGN, YOU ASSUME ALL RISK AND BEAR ALL RESPONSIBILITY AND LIABILITY, INCLUDING BUT NOT LIMITED TO, THE RESPONSIBILITY FOR ANY FEDERAL, STATE OR OTHER APPLICABLE REGULATORY REQUIREMENTS THAT APPLY TO THE MANUFACTURE, DISTRIBUTION, AND USE OF PAPRS. PANFAB SPECIFICALLY DISCLAIMS ALL WARRANTIES, EXPRESS, IMPLIED OR STATUTORY, INCLUDING IMPLIED WARRANTIES OF MERCHANTABILITY, FITNESS FOR A PARTICULAR PURPOSE, AND NONINFRINGEMENT.

© President and Fellows of Harvard College and The Massachusetts Institute of Technology, 2020.”

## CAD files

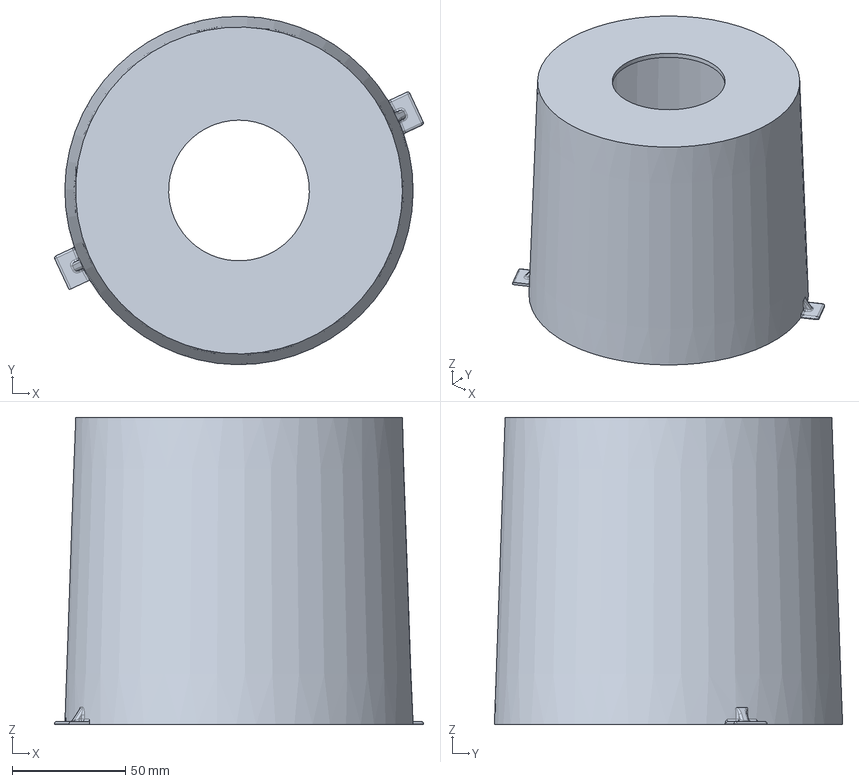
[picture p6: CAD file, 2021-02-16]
CAD Files/Commercial Milwaukee Filter/Filter Cover.step
162.6 x 153.5 x 135.5 mm

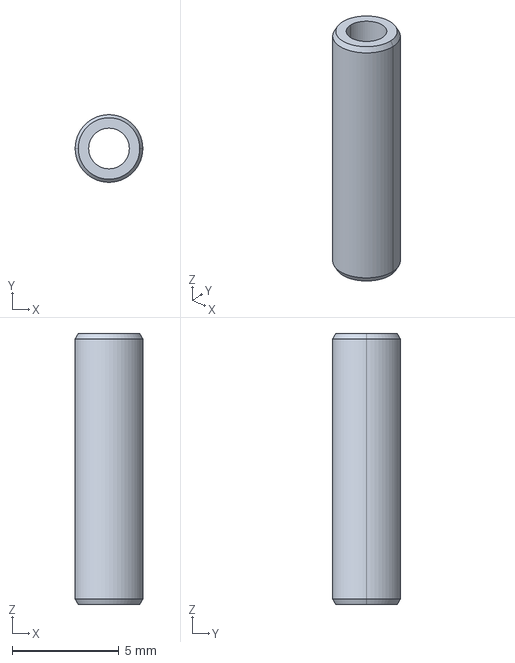
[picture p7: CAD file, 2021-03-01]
CAD Files/Custom Design/Venturi Port.stp
3.17 x 3.17 x 12.7 mm

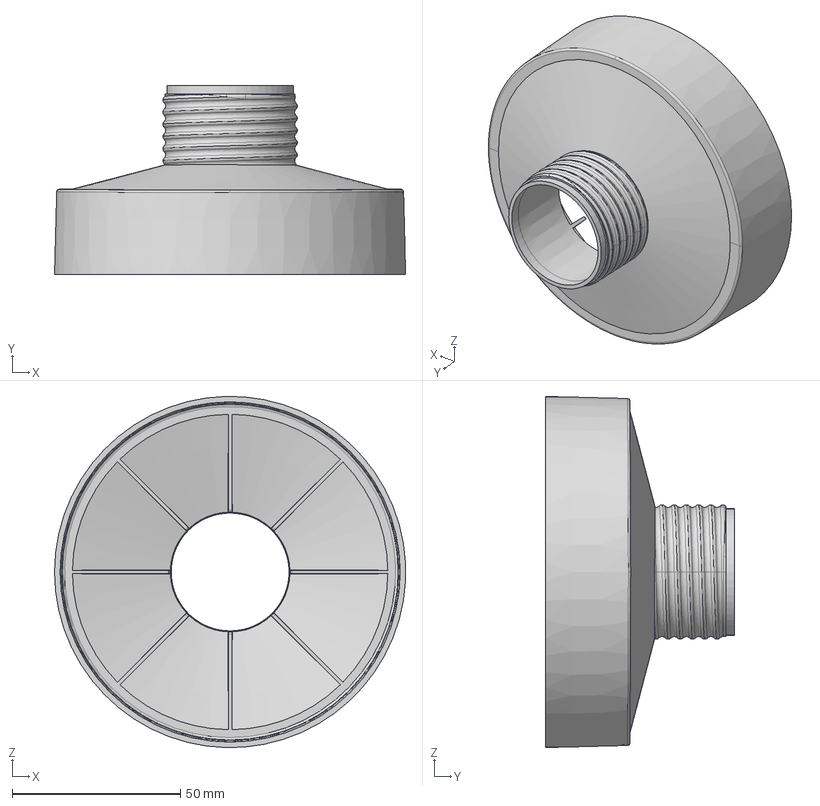
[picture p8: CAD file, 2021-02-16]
CAD Files/Custom Filter/Custom Filter Housing.step
104.4 x 56.3 x 104.5 mm

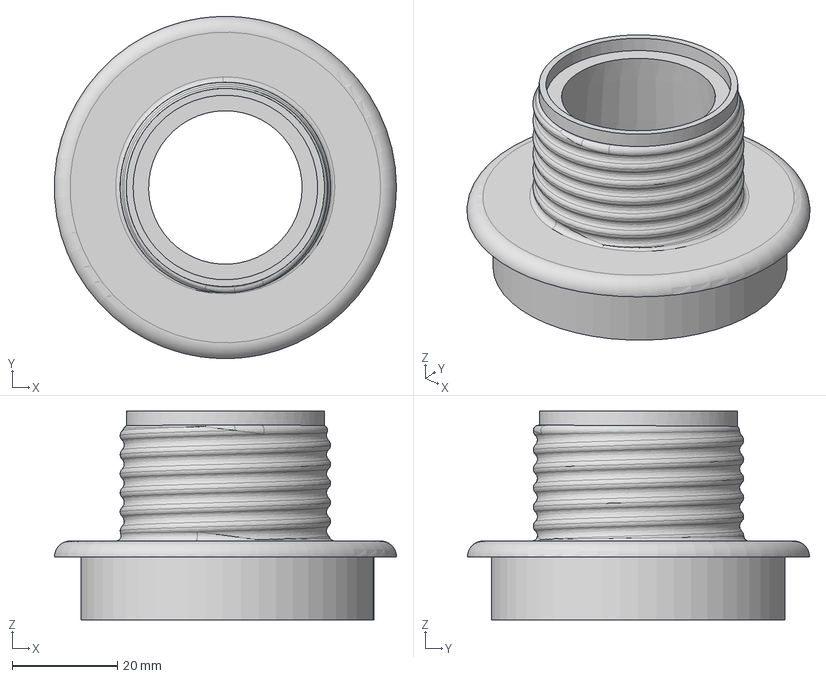
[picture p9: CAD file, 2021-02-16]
CAD Files/Commercial Milwaukee Filter/Filter Adapter.step
65.0 x 65.0 x 39.7 mm

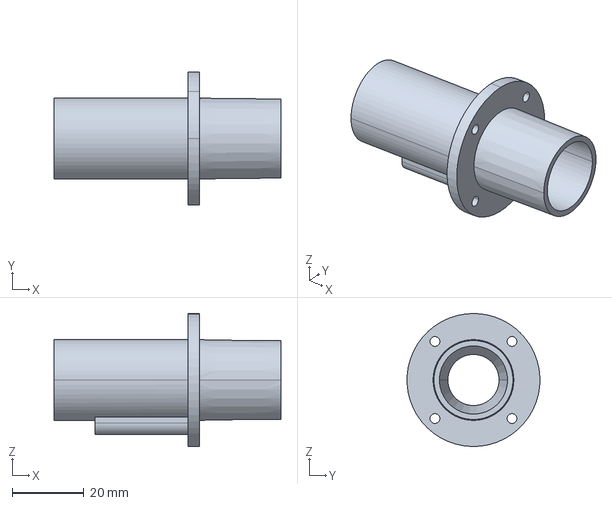
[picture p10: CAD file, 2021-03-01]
CAD Files/Custom Design/Venturi.stp
63.5 x 37.2 x 37.2 mm

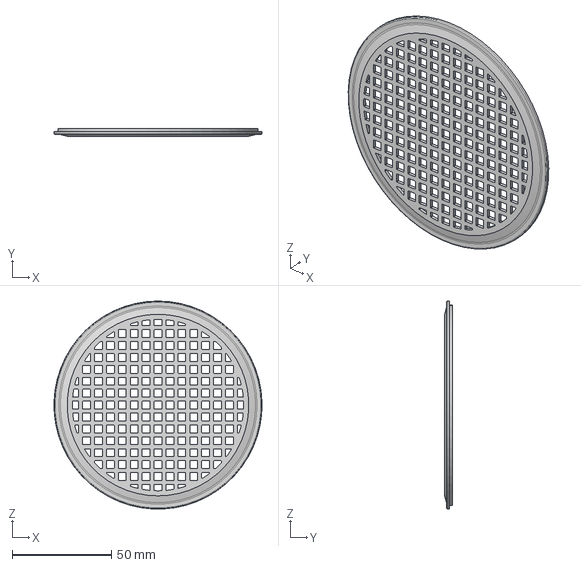
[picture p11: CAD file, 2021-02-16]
CAD Files/Custom Filter/Custom Filter Lid.step
104.8 x 3.91 x 104.7 mm

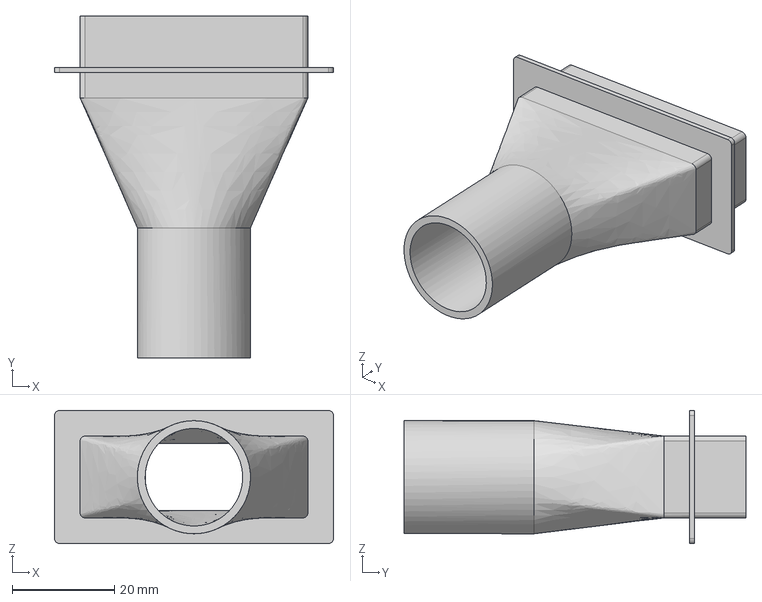
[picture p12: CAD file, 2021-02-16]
CAD Files/Custom Design/Blower Adapter.step
54.5 x 66.8 x 26.0 mm

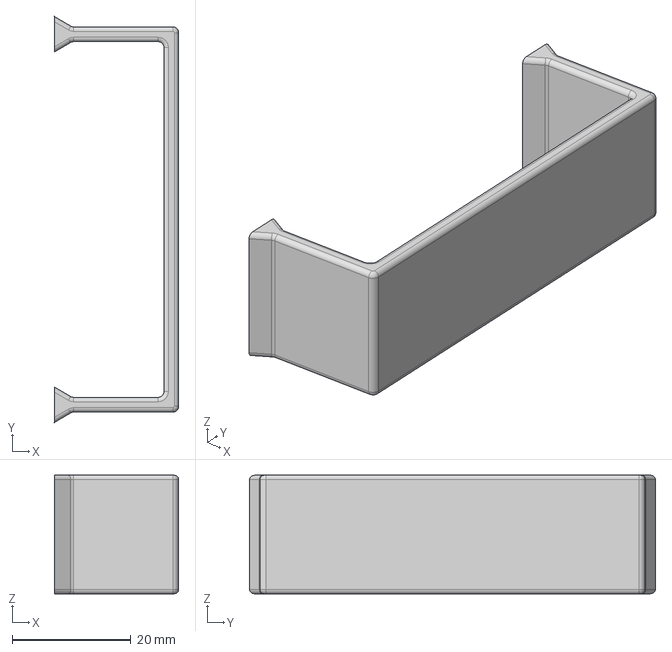
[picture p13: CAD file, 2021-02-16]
CAD Files/Pelican Case Design/Waist Strap Loop.step
21.0 x 68.5 x 20.0 mm

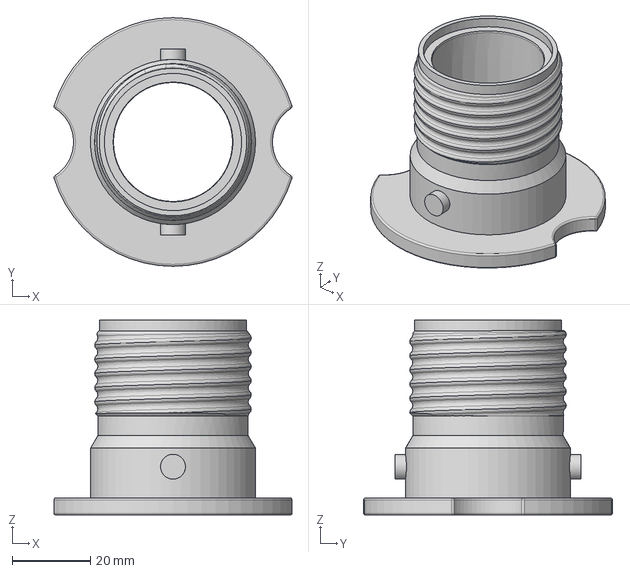
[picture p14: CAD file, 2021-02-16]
CAD Files/Custom Design/Hood Coupler.step
60.8 x 63.5 x 49.7 mm

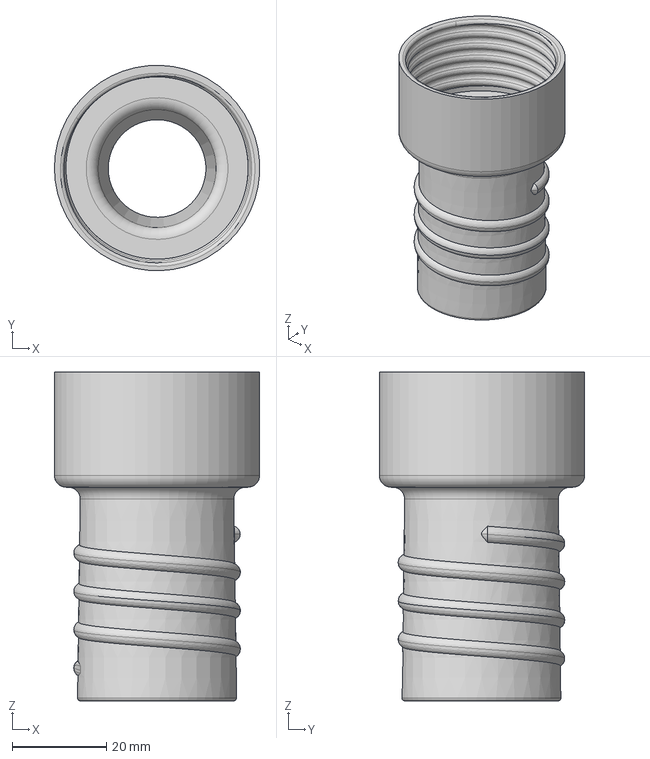
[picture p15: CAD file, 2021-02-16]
CAD Files/Pelican Case Design/Hose Adapter.step
43.4 x 43.5 x 69.7 mm

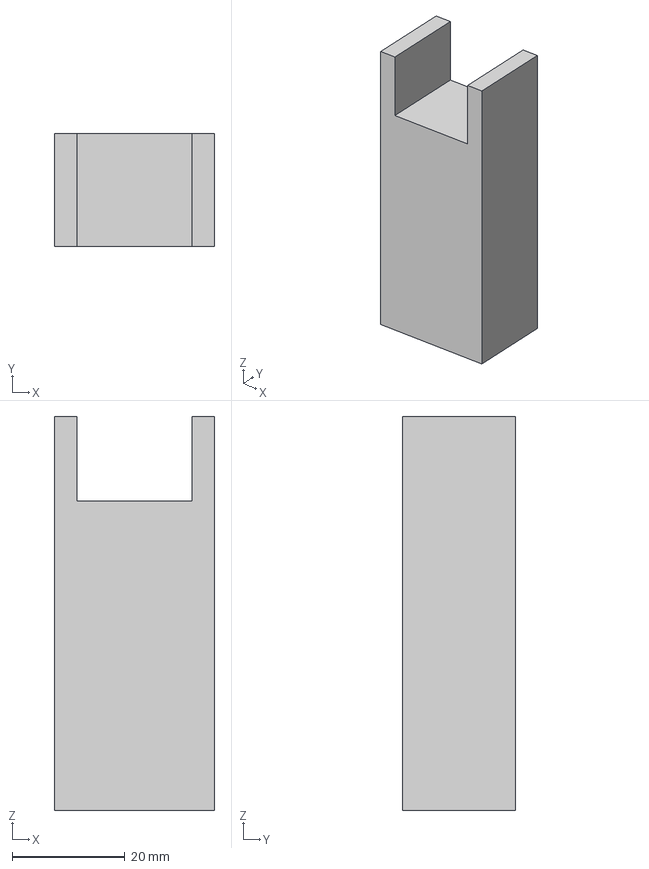
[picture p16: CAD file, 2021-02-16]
CAD Files/Custom Design/Custom Case Blower Mount.step
28.5 x 20.0 x 70.0 mm

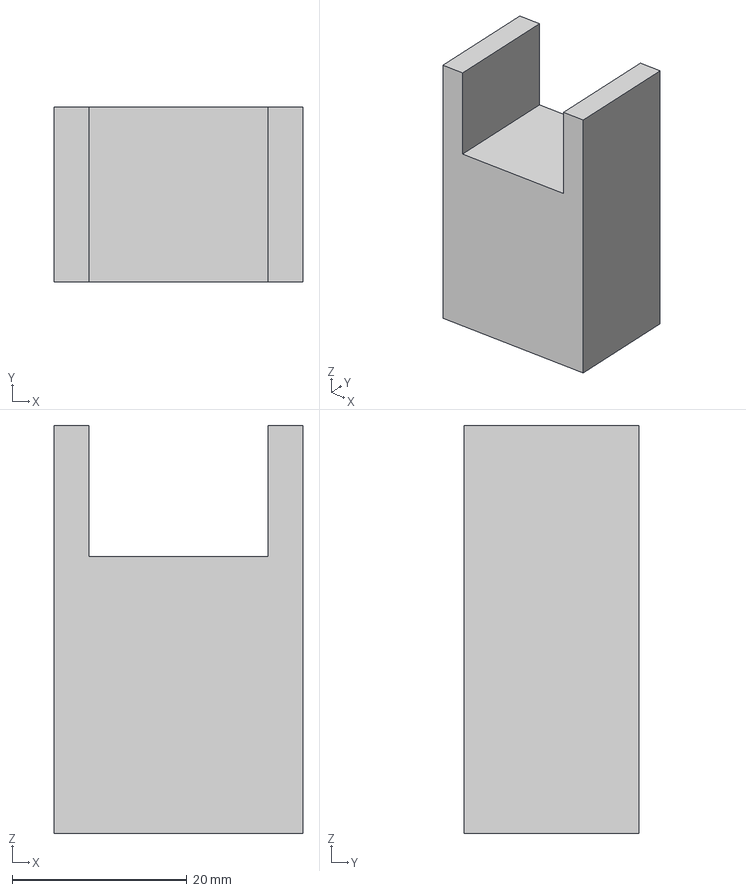
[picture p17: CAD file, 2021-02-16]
CAD Files/Pelican Case Design/Blower Mount.step
28.5 x 20.0 x 46.8 mm

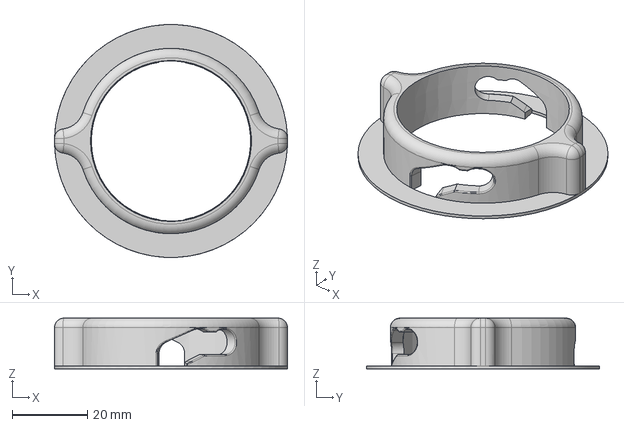
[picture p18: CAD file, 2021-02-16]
CAD Files/Custom Design/Locking Ring.step
62.0 x 62.0 x 13.5 mm

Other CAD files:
CAD Files/Custom Design/Lid.step
CAD Files/Pelican Case Design/Filter Insert.step
CAD Files/Pelican Case Design/Hose Insert.step

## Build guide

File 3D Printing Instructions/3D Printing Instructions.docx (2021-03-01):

3D Printing Instructions for PanFab PAPR Parts

Akshay Kothakonda¹ ,², *, Lyla Atta¹,³, *, Deborah Plana¹ ,⁴,⁵, *, Ferrous Ward¹ ,², *, Chris Davis¹,⁶, Avilash Cramer¹ ,⁵, Robert Moran¹ ,⁷, Jacob Freake¹,⁸, Enze Tian¹,⁹, Ofer Mazor¹,¹⁰, Pavel Gorelik¹,¹⁰, Christopher Van¹,¹¹, Christopher Hansen¹,¹², Helen Yang¹,¹³, Michael S. Sinha¹,¹³, Ju Li¹,¹⁴, Sherry H. Yu¹,¹⁵, Nicole R. LeBoeuf1,16, †, Peter K. Sorger1,4, †

¹ Greater Boston Pandemic Fabrication Team (PanFab) c/o Harvard-MIT Center for Regulatory Science, Harvard Medical School, Boston, MA, USA

²Department of Aeronautics and Astronautics, MIT, Cambridge, MA, USA

³Johns Hopkins University School of Medicine, Baltimore, MD, USA

⁴Harvard Ludwig Cancer Research Center and Department of Systems Biology, Harvard Medical School, Boston, MA, USA

⁵ Harvard-MIT Division of Health Sciences & Technology, Cambridge, MA, USA

⁶GenOne Technologies, Cambridge, MA, USA

⁷Mine Survival, Panama City Beach, FL, USA

⁸Fikst Product Development, Woburn, MA, USA

⁹Beijing Key Laboratory of Indoor Air Quality Evaluation and Control, Department of Building Science, Tsinghua University, Beijing, China

¹⁰Research Instrumentation Core Facility, Harvard Medical School, Boston, MA, USA

¹¹Borobot, Middleborough, MA, USA

¹²Harvard Graduate School of Design, Cambridge, MA, USA

¹³Harvard-MIT Center for Regulatory Science, Harvard Medical School, Boston MA, USA

¹⁴Department of Nuclear Science and Engineering and Department of Materials Science and Engineering, MIT, Cambridge, MA, USA

¹⁵Department of Dermatology, Yale School of Medicine, New Haven, CT USA

¹⁶ Department of Dermatology, Center for Cutaneous Oncology, Brigham and Women’s Hospital and Dana-Farber Cancer Institute, Boston, MA, USA

*These authors contributed equally to this work

†Co-corresponding authors. E-mails: nleboeuf@bwh.harvard.edu; peter_sorger@hms.harvard.edu cc: Maureen_Bergeron@hms.harvard.edu;

ORCID IDs:

Akshay Kothakonda, 0000-0001-5424-4228

Lyla Atta, 0000-0002-6113-0082

Deborah Plana, 0000-0002-4218-1693

Avilash Cramer, 0000-0003-0014-8921

Jacob Freake, 0000-0002-5198-835X

Enze Tian, 0000-0001-6410-5360

Christopher Van, 0000-0003-3262-964X

Christopher Hansen, 0000-0002-6640-2745

Ju Li, PhD, 0000-0002-7841-8058

Helen Yang, 0000-0002-9455-5300

Michael S. Sinha 0000-0002-9165-8611

Sherry H. Yu: 0000-0002-1432-9128

Nicole R. LeBoeuf, MD, MPH, 0000-0002-8264-834X

Peter Sorger, PhD, 0000-0002-3364-1838

INTRODUCTION

The PanFab PAPR unit was designed in response to the personal protective equipment (PPE) shortages caused by the COVID-19 pandemic. As such, viable tested prototypes were printed in low-cost, readily available materials such as Polyethylene terephthalate – glycol (PETG) polyester polymer on a high-speed fused deposition modeling (FDM) printer. PETG was chosen as the prime material candidate based on preliminary testing for layer adhesion, total part strength, impact resistance, ease of printing, and viability of post-processing. MSLA Resin printing was used to fabricate smaller parts with tighter tolerances. The primary resin used was SirayaTech Blu resin (polyurethane – acrylate copolymer).

While all the prototypes for PanFab Custom and Commercial PAPR’s used in design validation testing were 3D printed, all the parts have been optimized for injection molding for high volume production.

This document presents printing settings that were used by the PanFab team in prototyping the Custom PAPR and Commercial PAPR designs. Note that the settings and material should be optimized for the specific printer used in printing the parts.

PANFAB CUSTOM DESIGN PAPR HOUSING

The PanFab PAPR Custom Design housing has the following components:

- Lid, has integrated female NATO 40 mm threaded connecter for filters
- Bin, which attaches to it all the components to power and control the blower

Bin with Gasket Recess

The housing parts and Milwaukee Filter Cartridge Cover were printed on a RailCore II 300ZLT FDM 3D printer. The “bin” and “lid” parts must be nominally air-tight, so all air handled by the device must first pass through filters. The printed part can maintain function even without dense infill, but top and bottom layers must be increased, and slight over extrusion (or top layer “ironing” is recommended). Layer height of 300 microns was used with 15% rectilinear infill. Increase vertical shells to 4 for increased part strength. This part is designed to minimize supports, but still requires support on the gasket seal overhang, and threaded outlet. The threads on the outlet will need to be manually finished, and this can be accomplished with a cylindrical file (or m3 threaded rod, if necessary). Additional air tightness can be provided with a conformal coating of resin or other sealant. Print in default orientation with the interior of the part facing upwards.

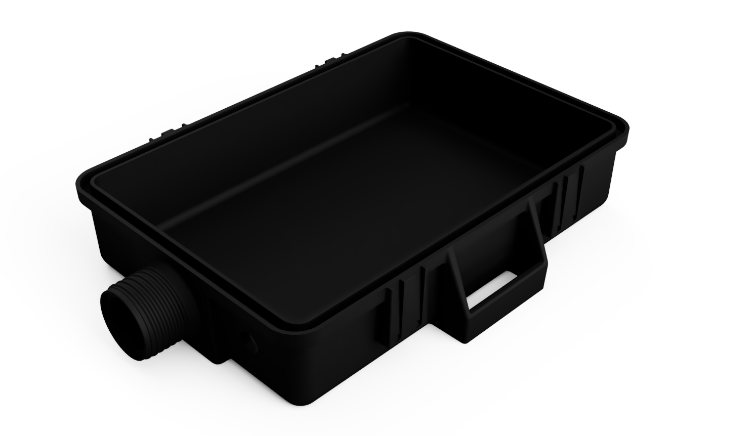
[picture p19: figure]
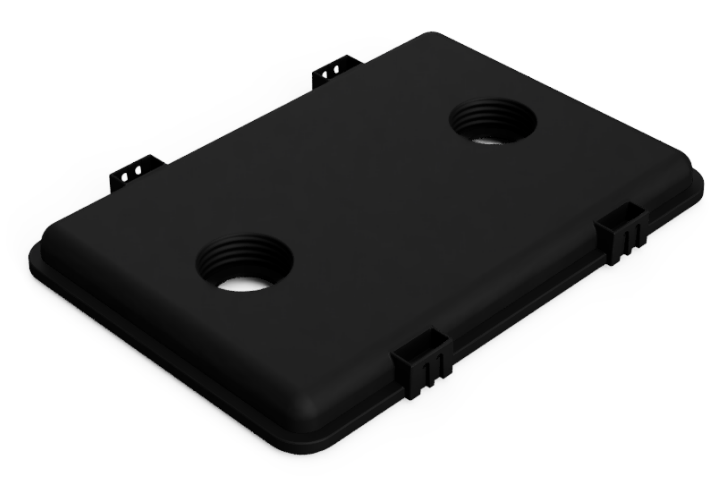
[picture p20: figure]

Lid with Tongue Feature

Settings similar to “Bottom with Gasket Recess.” Print with the surface visible in the figure to the right on the build plate (larger opening on threaded holes toward build plate)

COMMERCIAL MILWAUKEE FILTER CARTRIDGE COVER

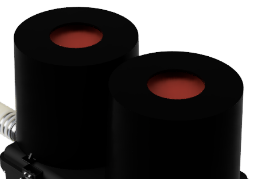
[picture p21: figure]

This part covers and protects the filter media of the Milwaukee commercial filter cartridge from damage. Print this part with flat surface on build plate, 100% infill, two walls. This is not a structural part, and therefore can be printed much thinner than either the bottom with gasket recess or the lid.

ALL OTHER PARTS

In addition to the parts discussed, there are several smaller parts such as the hose adapter, hood coupler, locking ring, filter inserts, hose insert, blower adapter, blower mounts, and belt loops. Print these in resin for optimal air tightness. Resin used was SirayaTech Blu, on Anycubic LCD 3D printers (Photon S and Mono X). The resin must be optimized for the printer being used. Parts can also be printed in FDM, but this was not tested by our team for NIOSH-equivalent tests.

© President and Fellows of Harvard College and The Massachusetts Institute of Technology, 2020.

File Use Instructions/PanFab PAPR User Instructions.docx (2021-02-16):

# PanFab PAPR User Instructions

PanFab has developed two PAPR designs for use by healthcare workers amidst the COVID-19 pandemic. One PAPR uses a custom enclosure designed and engineered for this particular project. The other PAPR uses a modified commercial Pelican case as the enclosure. Most other parts in the two PAPR’s are the same. The instructions here, while described only for the custom enclosure PAPR, apply to the Pelican case PAPR as well, unless otherwise noted. Also note that either enclosure can be used with either filter (custom filter or commercial Milwaukee filter).

# Overview

This section introduces the PAPR construction and operation.

## Parts in the PAPR’s

The PAPR’s consist of the following parts/assemblies:

- Enclosure (with enclosure gasket and waist belt)
  - Custom enclosure consists of two parts- a bin and a lid
  - Custom enclosure has separately assembled latches)
- 2 x Filters
- 2 x Filter covers (for Milwaukee HEPA Filter)
- Blower
- Blower Adapter
- 1” Silicone tube (to connect blower adapter to venturi)
- Venturi (with ports)
- 7/32” Silicone tube (to connect venturi ports with differential pressure sensor)
- Switch
- Battery Pack
- Battery Connector
- Potentiometer
- Buzzer
- Microcontroller (with soldered electronic components)
- Hose (integrated with threaded hose adapters on both ends)
- 4 x Face gaskets (2 for filter inlet and 2 for hose adapters)
- Hood Coupler
- Locking Ring
- Hood
- Head Strap
- Battery charger

## PAPR Construction

Figure 1 below shows the custom enclosure with all the parts labelled.

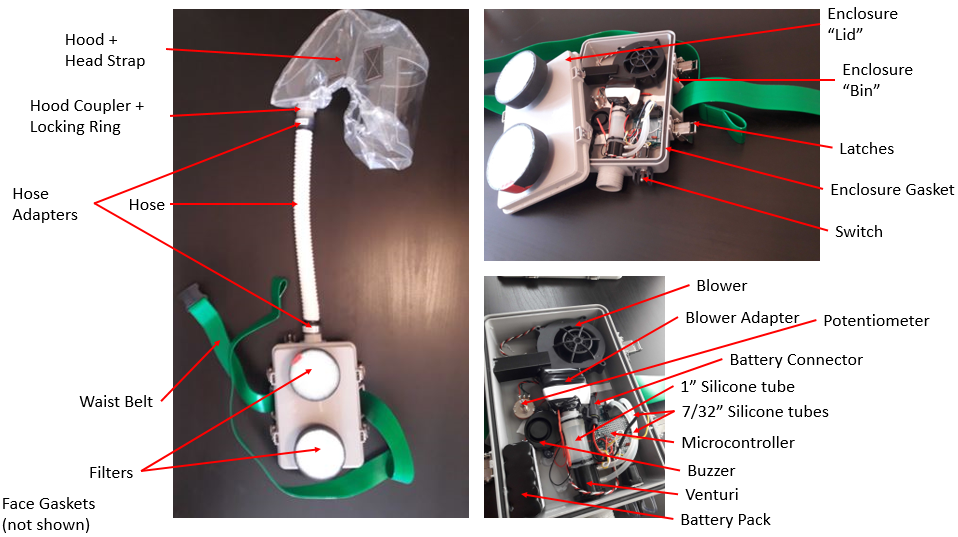
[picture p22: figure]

Figure 1. PanFab PAPR components

The Enclosure “lid” and “bin” are closed together and locked using latches. An enclosure seal in the perimeter groove on the bin for custom enclosure, and on the lid for Pelican enclosure, seals the enclosures. In the case of Pelican enclosure, only two latches are present and the enclosure has a “clamshell” design. The two filters are screwed into the threaded holes on the enclosure lid for the custom enclosure, and on the side opposite to the lid on the Pelican enclosure. The face gaskets in these holes provide sealing. A waist belt assembled with the enclosure enables donning the PAPR.

The hose has two hose adapters permanently installed on either end- one connects to the enclosure outlet and the other connects to the hood inlet. The hose is connected to the enclosure and hood (at hood coupler) by screwing the parts together. Again, face gaskets ensure sealing at these joints. The locking ring forms a tight connection between the hood coupler and the hood. The hood is worn over the head and is secured to the head using a tight fitting head strap, joined by Velcro strips.

A switch on the enclosure turns on/off the system. A microcontroller (Arduino Uno board connected to a proto-shield) forms the control system of the PAPRs. The blower, battery, potentiometer, buzzer, switch, and venturi are all connected to the microcontroller. The battery connector connects the battery to the switch. When the connector is closed and the switch is turned on, the microcontroller and blower are turned on. The blower sucks in outside air through the filters, cleaning it. The clean air is then pushed through to the hood for breathing. The air then escapes out through holes in the hood. The blower adapter allows for connecting blower outlet to venturi inlet through a 1” OD silicone tube. The silicone tube provides compliance in blower-venturi alignment. The silicone tube is joined to the venture. At the exit of venture, the air flows to the hose through enclosure outlet.

The venturi has two ports which are connected to a differential pressure sensor mounted on the microcontroller, through 7/32” silicone tubes. The differential pressure sensor is used to estimate the flow rate. When the flow rate drops below 230 LPM for 10 consecutive seconds, the buzzer goes off to alert the wearer of low flow rate. The potentiometer is used to vary the flow rate as per user comfort.

# Use Procedure

This section describes the steps involved in using the PAPR.

1. Open the enclosure by opening the latches. On the custom case, the latches are opened by pressing on the safety catches and then lifting the lower tab. On the Pelican case, the latches are opening by pressing the release button in the middle and lifting the tabs. Ensure that the enclosure gasket is sitting in its groove and is not falling out of it. Also ensure that the battery connector is connected.
2. Place the enclosure lid over the enclosure bin, ensuring none of the wires stick outside the enclosure, and close down the latches. See Figure 2 below.

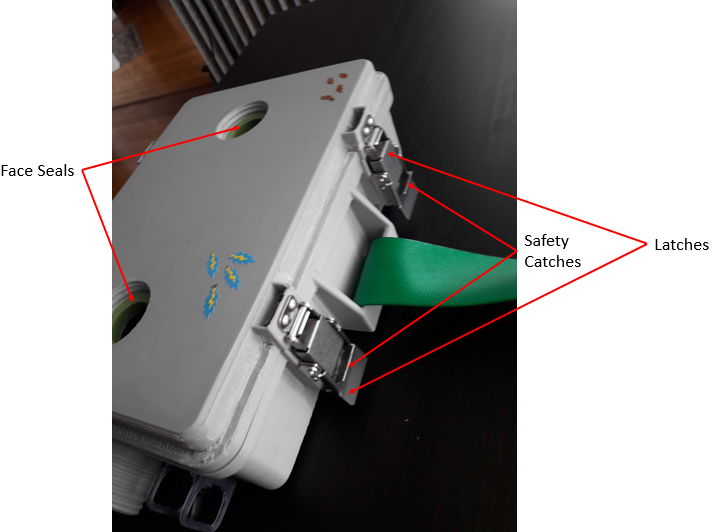
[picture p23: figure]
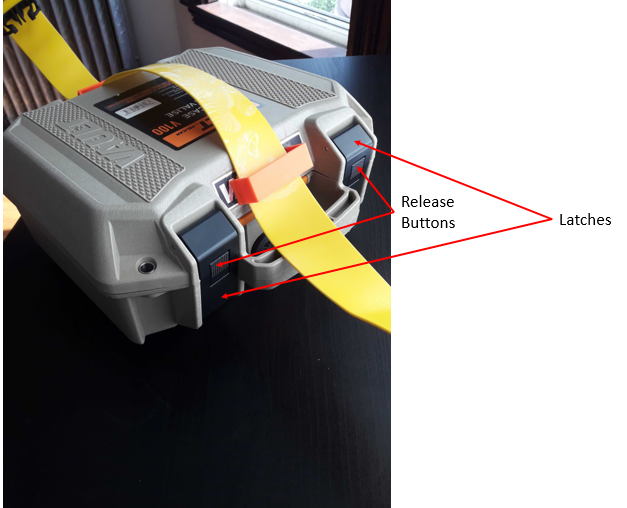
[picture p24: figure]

Figure 2. Enclosure Lid closure

3. Check that the face seals are present in the internal threaded holes on the enclosure and are not raised from their gasket seats (gasket seats are flat surfaces at the bottom of the internal threads where the face seals sit). If the seals are raised, push down on them until they make uniform contact with the gasket seats.
4. Filter installation.
  a. Custom filters: Screw in the two filters onto the lid of custom enclosure, as shown in Figure 3. For Pelican enclosure, the filter inlet holes are on the face opposite to the lid. Hand-tighten the filters until there is significant resistance to further turning. Do not over-torque the filters.

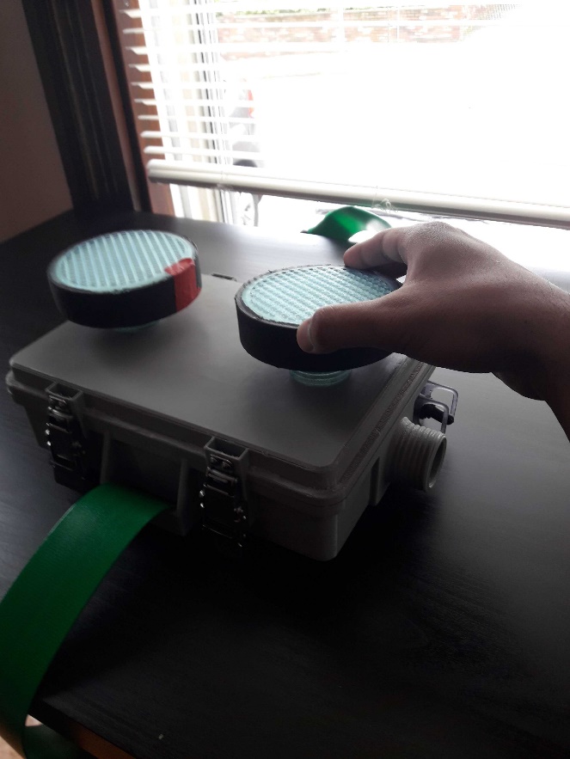
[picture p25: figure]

Figure 3. Custom Filter Installation

  b. Milwaukee filters: While installing the Milwaukee filters, always use the bottom end cap of the filter to tighten; see Figure 4 below. Screw in the two filters into the threaded holes. Hand-tighten the filters until there is significant resistance to further turning. Do not over-torque the filters.

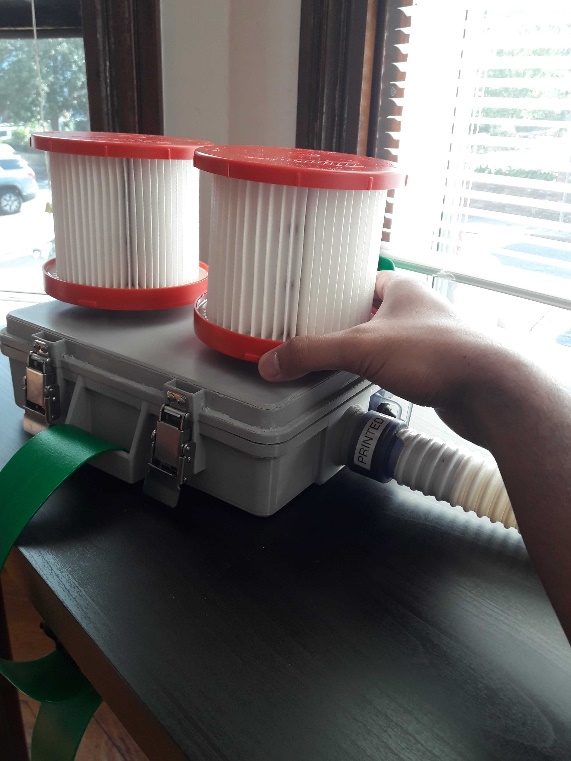
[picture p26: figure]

Figure 4. Commercial Filter Installation

Slide the two filter covers over the filters and rotate them about their axes so that the two tabs on each cover makes contact with the top surface of the enclosure. Use a strip of double-sided mounting tape for each cover tab and press down the cover on the enclosure to make a good bond. Again, ensure that the mounting tape under the tabs make good surface contact with the enclosure surface. Also be careful in positioning the covers over the two filters so that there is enough room for the two covers; it is advised to put on the mounting tape after sliding both covers over, to ensure compliance. Figure 5 below shows the PAPR enclosure with Milwaukee filters and filter covers installed.

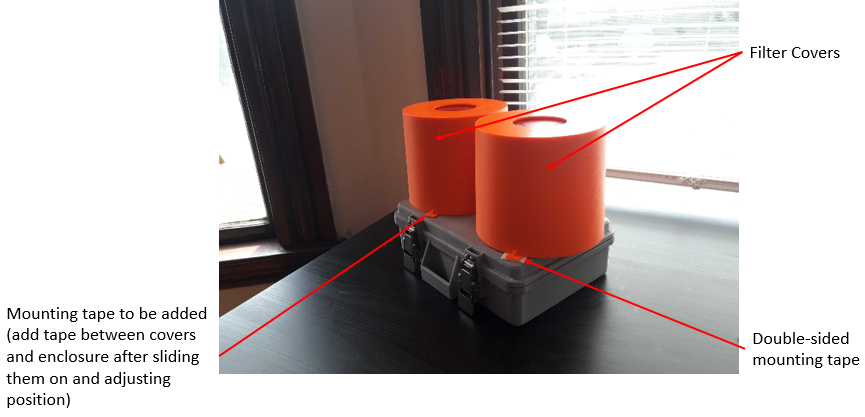
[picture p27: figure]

Figure 5. Commercial Filter Cover installation

5. Once the face seals are inspected on each hose adapter as per step 3 above, screw the hose onto the outlet of the enclosure, as shown in Figure 6. Hand-tighten the hose adapter until there is significant resistance to further turning. Do not over-torque the hose adapter. Always apply torque on the adapter, and not on the hose. Ensure the correct hose is used for a given PAPR enclosure.

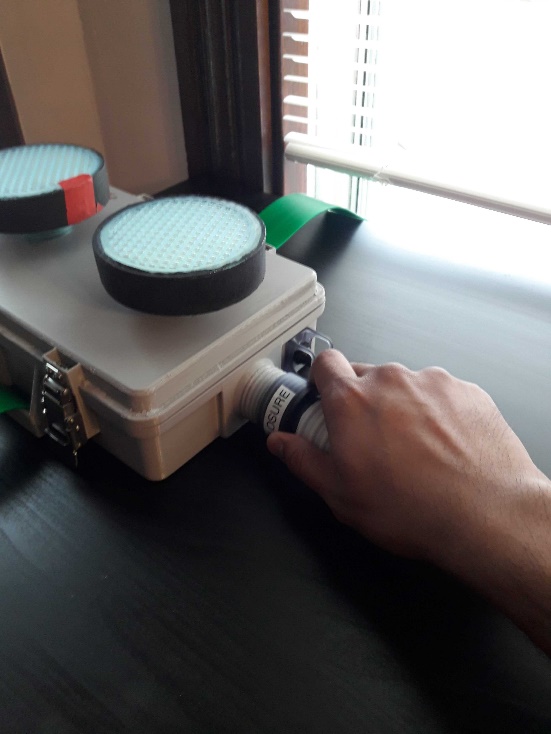
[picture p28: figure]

Figure 6. Hose connection

6. Pass the hood coupler through the circular hole at back of the hood in such a way that the threaded part faces out of the hood. Make sure the two small cylindrical tabs pass through the hole. See Figure 7 below.

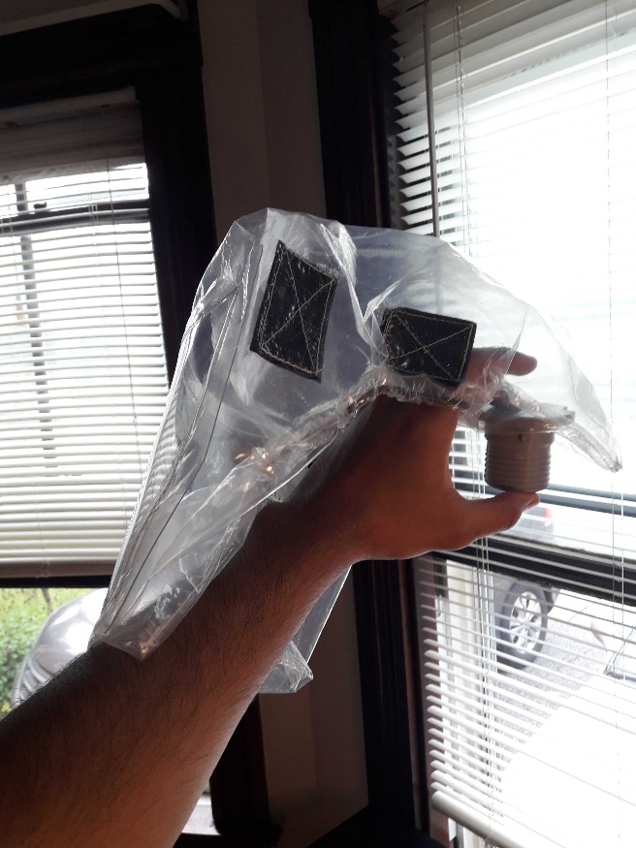
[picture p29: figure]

Figure 7. Hood Coupler and hood connection

7. Slide the locking ring over the hood coupler. The tabs on the hood coupler should slide into the slot on the locking ring. However, do not turn the locking ring to lock it. The assembly at this step will look like Figure 8 below.

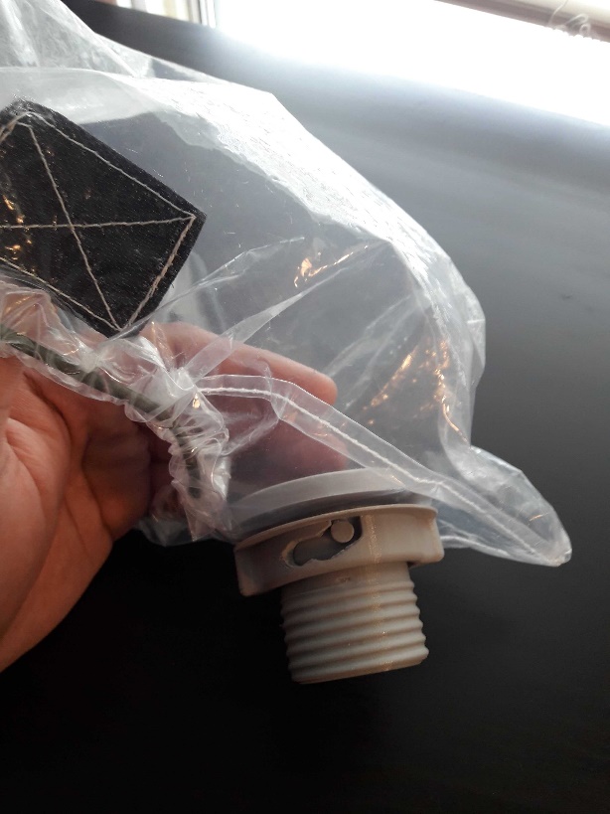
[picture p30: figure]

Figure 8. Hood Coupler and Locking Ring connection

8. With the locking ring still “unlocked”, screw the hood coupler into the other end of the hose (into the hose adapter), as shown in Figure 9 below. Hand-tighten the hood coupler until there is significant resistance to further turning. Do not over-torque the hood coupler. Do not apply torque on the hose.

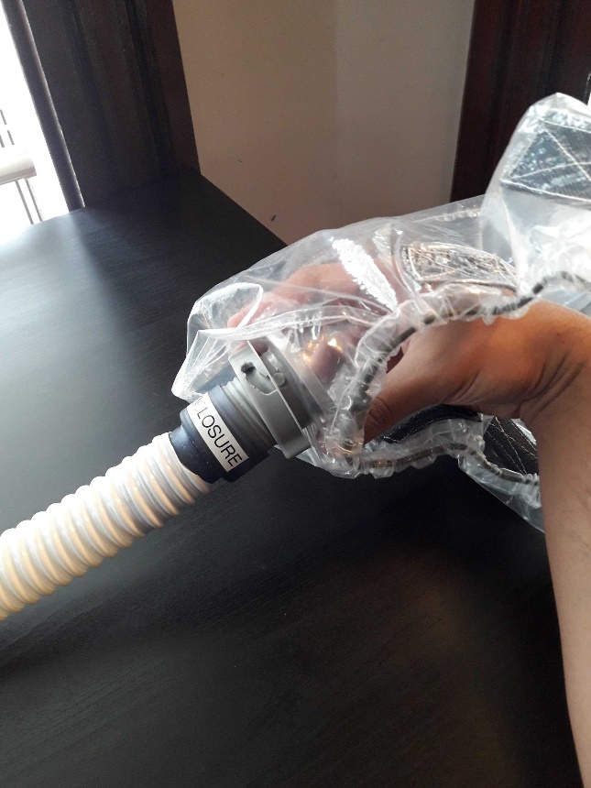
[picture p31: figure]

Figure 9. Hood Coupler and Hose Adapter Connection

9. Orient the hood such that the “face” of the hood faces away from the filter inlet. i.e. the enclosure is worn on lower back such that the filters face away from the body backward and the hood faces forward.
10. Once the hood is oriented as per step 9, lock the locking ring onto the hood coupler by turning it clockwise. Ensure to lock it only when the cylindrical tabs on the hood coupler are out of the hood, as per step 6. The hood coupler with locking ring locked will be as shown in Figure 10.

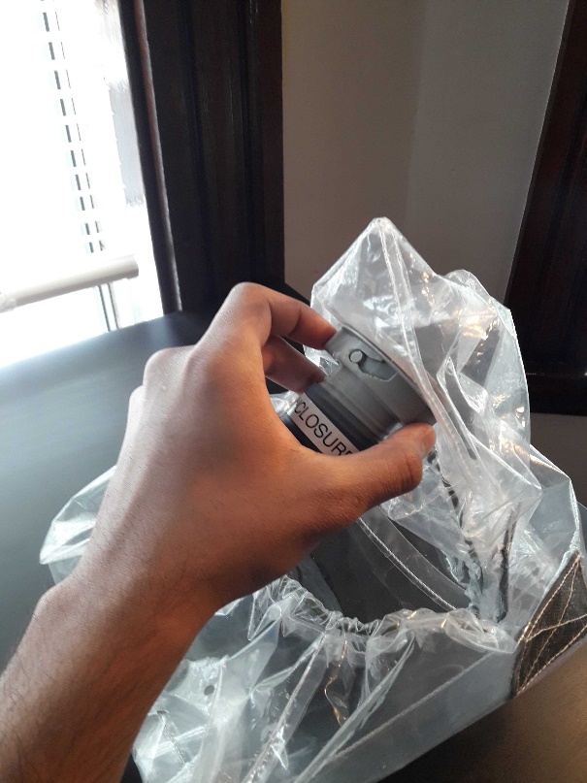
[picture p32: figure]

Figure 10. Locking Ring locked on Hood Coupler

11. To don the PAPR, first set the enclosure on a waist-high table, with filters facing down. Then, carefully lift the enclosure using the belt straps towards lower back. Close the buckle of the belt and adjust the tightness as required. Tuck in the excess strap length into the tightened strap. Figure 11 shows the PAPR enclosure donning.

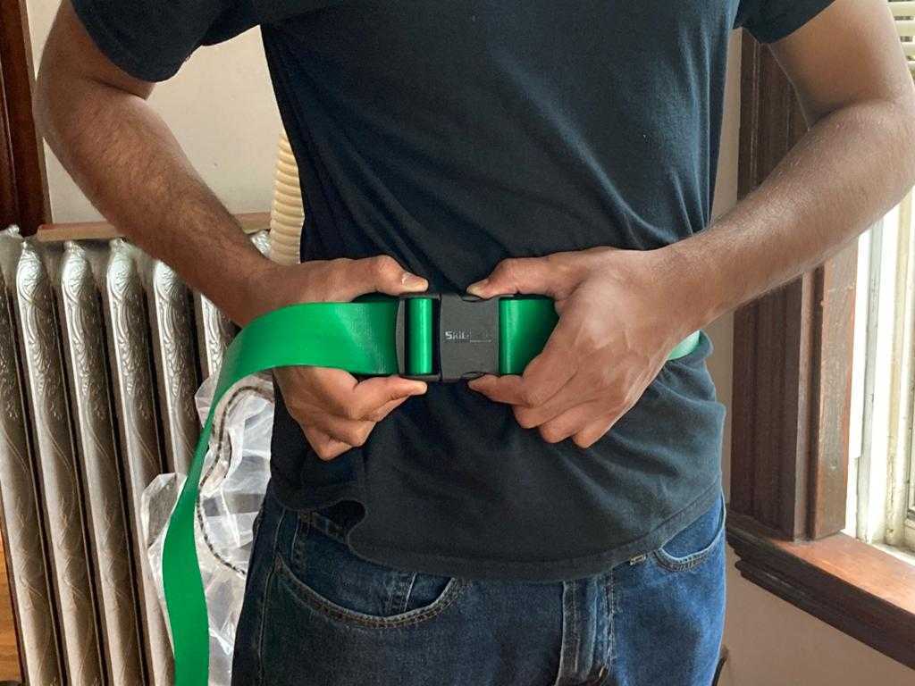
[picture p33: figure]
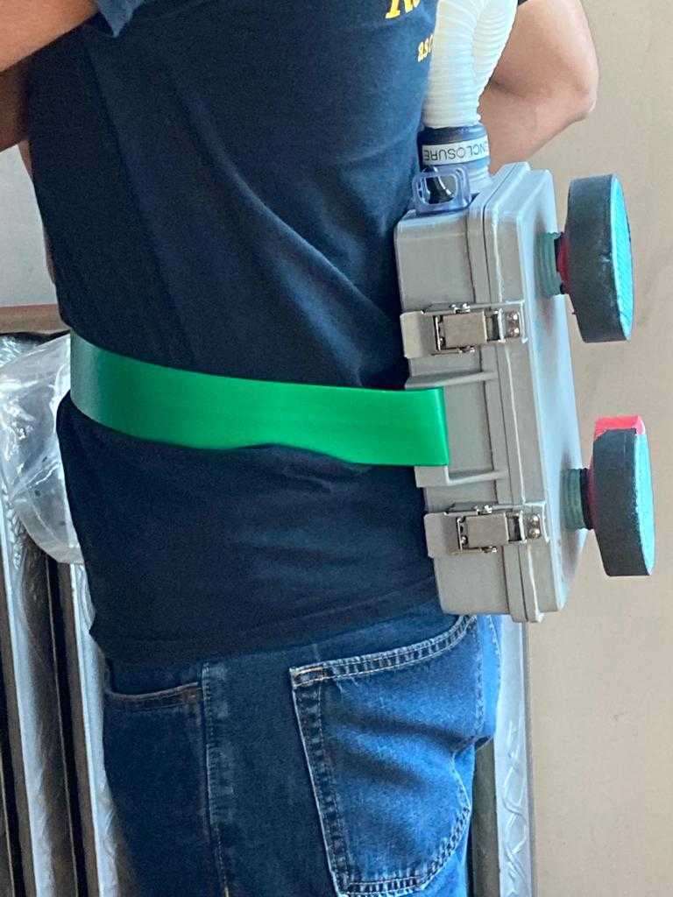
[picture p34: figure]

Figure 11. PAPR Enclosure Donning

12. Put on the head strap. There are 7 velcro strips on the head strap in total. 3 of them are used in tightening the head strap on the head, while the other 4 connect to corresponding strips in the hood. The tightening (T) strips and the strips connecting to hood are labelled as shown in Figure 12 below. The 4 strips connecting to hood are labelled based on their position on the user’s head.

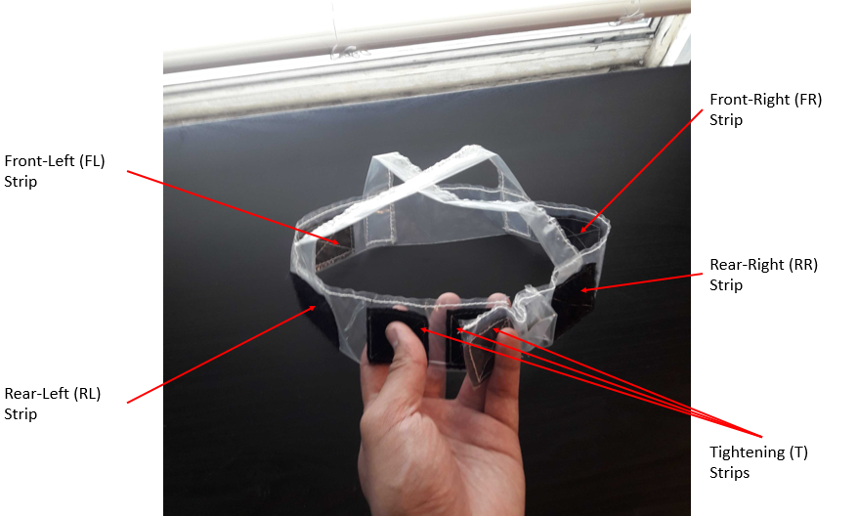
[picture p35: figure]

Figure 12. Velcro strips on head strap

Ensure the Velcro strips are facing outward, as shown in the Figure 12 above. Un-couple the tightening strips and place the head strap on the head, with two hands on the rear part of the head strap (the rear part has the 3 T strips). Couple the T strips after having tightened the head strap around the head to required tightness, as shown in Figure 13. The coupled T-strips should be at the rear of the head, as per figure below. The tightness should be enough so that the hood and the head strap don not fall off.

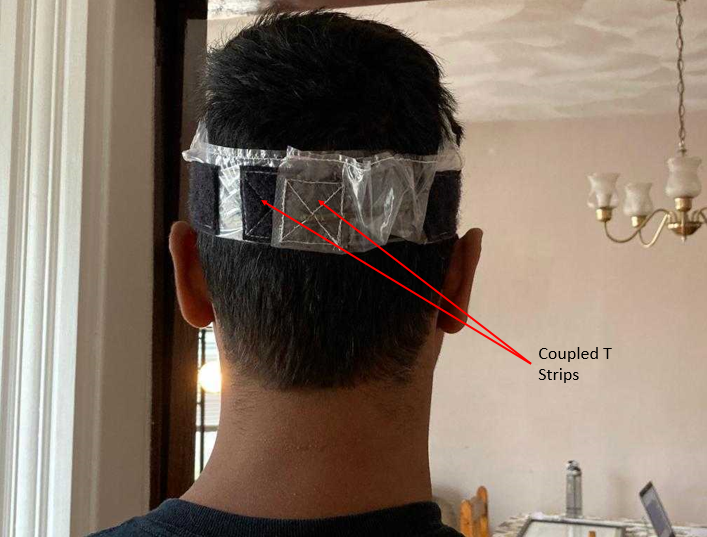
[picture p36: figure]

Figure 13. Head strap donning

13. Put on the hood. There are 4 velcro strips on the inside of the hood that correspond to FR, FL, RR, RL strips on the head strap. The 4 strips on the hood are labelled in Figure 14 below.

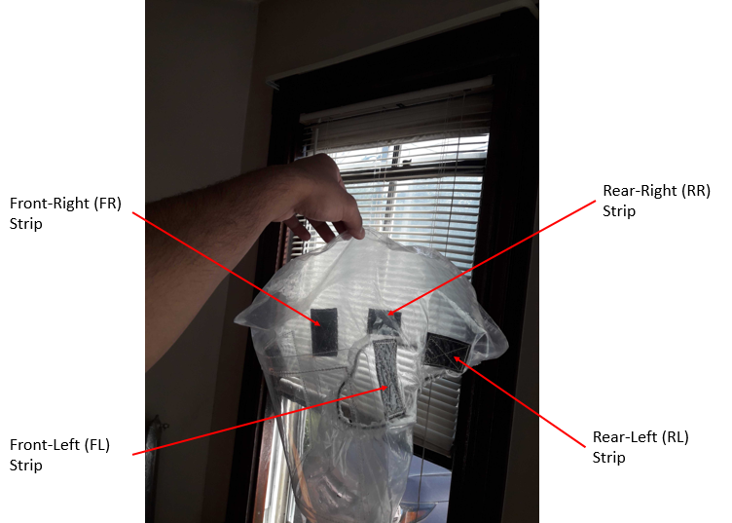
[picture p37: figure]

Figure 14. Velcro strips on the hood

With two hands, locate RR and RL strips on the hood and connect them to corresponding strips on the head strap. Press down tightly on the Velcro to ensure the connection is secure. Then, locate FR and FL strips on the hood with two hands and connect them to corresponding strips on the head strap. Once the strips are securely connected, pull down the hood so that the lower part of the elastic cord (in the hood) rests below the lower jaw and the part of the elastic cord just below the Velcro strips rests above the ears. Ensure tight fit everywhere and adjust for comfort. After donning the hood, the system should look on the wearer as per Figure 15 below.

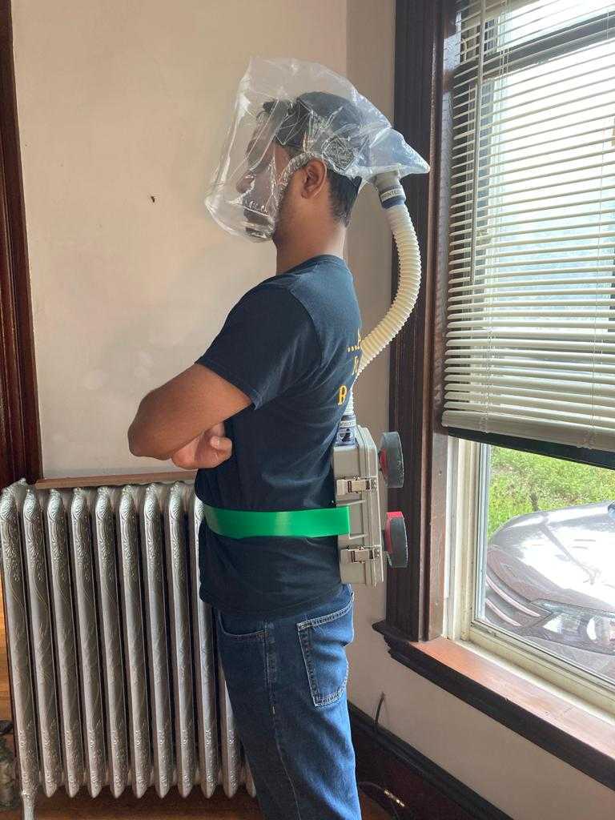
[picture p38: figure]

Figure 15. Fully donned PAPR

14. To turn on the PAPR, reach behind and turn on the switch, as shown in Figure 16.

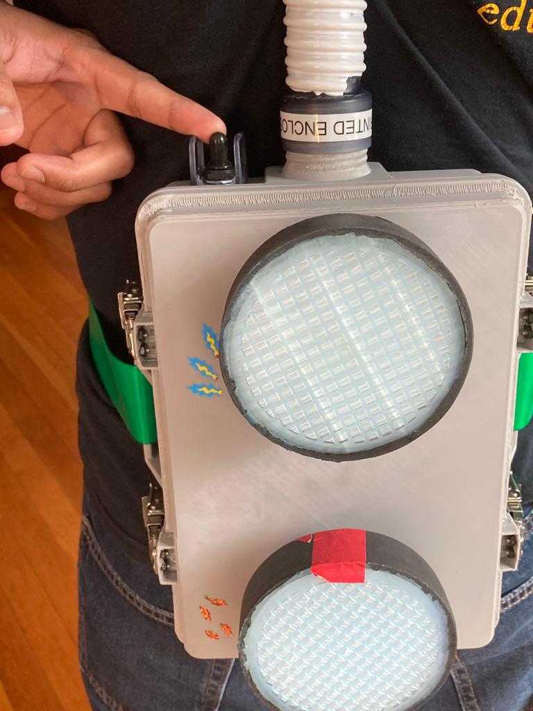
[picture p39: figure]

Figure 16. Turning on/off the PAPR

15. Doffing the PAPR is carried out by reversing the steps above.
16. The potentiometer knob (see Figure 1) can be turned clockwise to increase flow rate or counter-clockwise to reduce the flow rate. Adjust the flow rate to a comfortable level. Note: too little of a flow rate will make the buzzer go off.
17. Always wait 10 seconds after turning on the PAPR to go into a hazardous environment. If the buzzer goes off after 10 seconds of turning on the PAPR, either the flow rate needs to be increased, the filter needs to be replaced (due to excessive clogging), or the battery needs to be recharged. Note that the operational time on full charge, with maximum flow rate (potentiometer turned all the way), is nearly 4 hours, after which the battery would need to be recharged.
18. The battery is recharged using a charger provided. The battery can be charged either at 0.9A or 1.8A. Higher charging current will charge the battery faster, but may cause heating in the battery. It is advised to charge the battery at 0.9A.

To charge the battery, open the lid as per step 1. Then, disconnect the battery to the switch by de-coupling the battery connector. Be careful so as to not knock over other parts during this disconnect process. Once disconnected, couple the half of the connecter connected to the battery, to the mating connector half on the charger. Set the charging voltage to either 0.9A or 1.8A. Plug in the other end of the charger to a power outlet. When charging, the red LED on the charger will turn on. When the battery is fully charged, the green LED on the charger will turn on. When charging is complete (which takes a little less than 3 hours at 0.9A), disconnect the connector to the battery and reconnect the battery to the switch. See Figure 17.

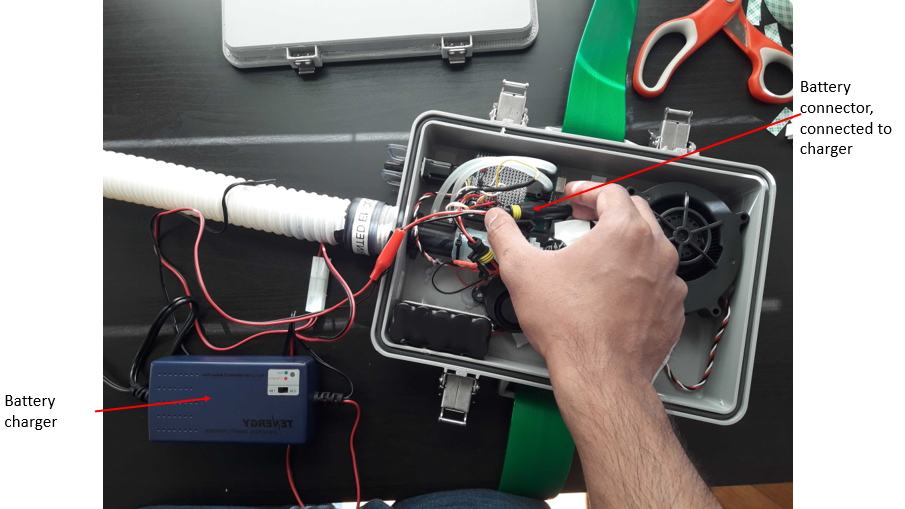
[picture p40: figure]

Figure 17. Connection of battery pack to battery charger

© President and Fellows of Harvard College and The Massachusetts Institute of Technology, 2020.

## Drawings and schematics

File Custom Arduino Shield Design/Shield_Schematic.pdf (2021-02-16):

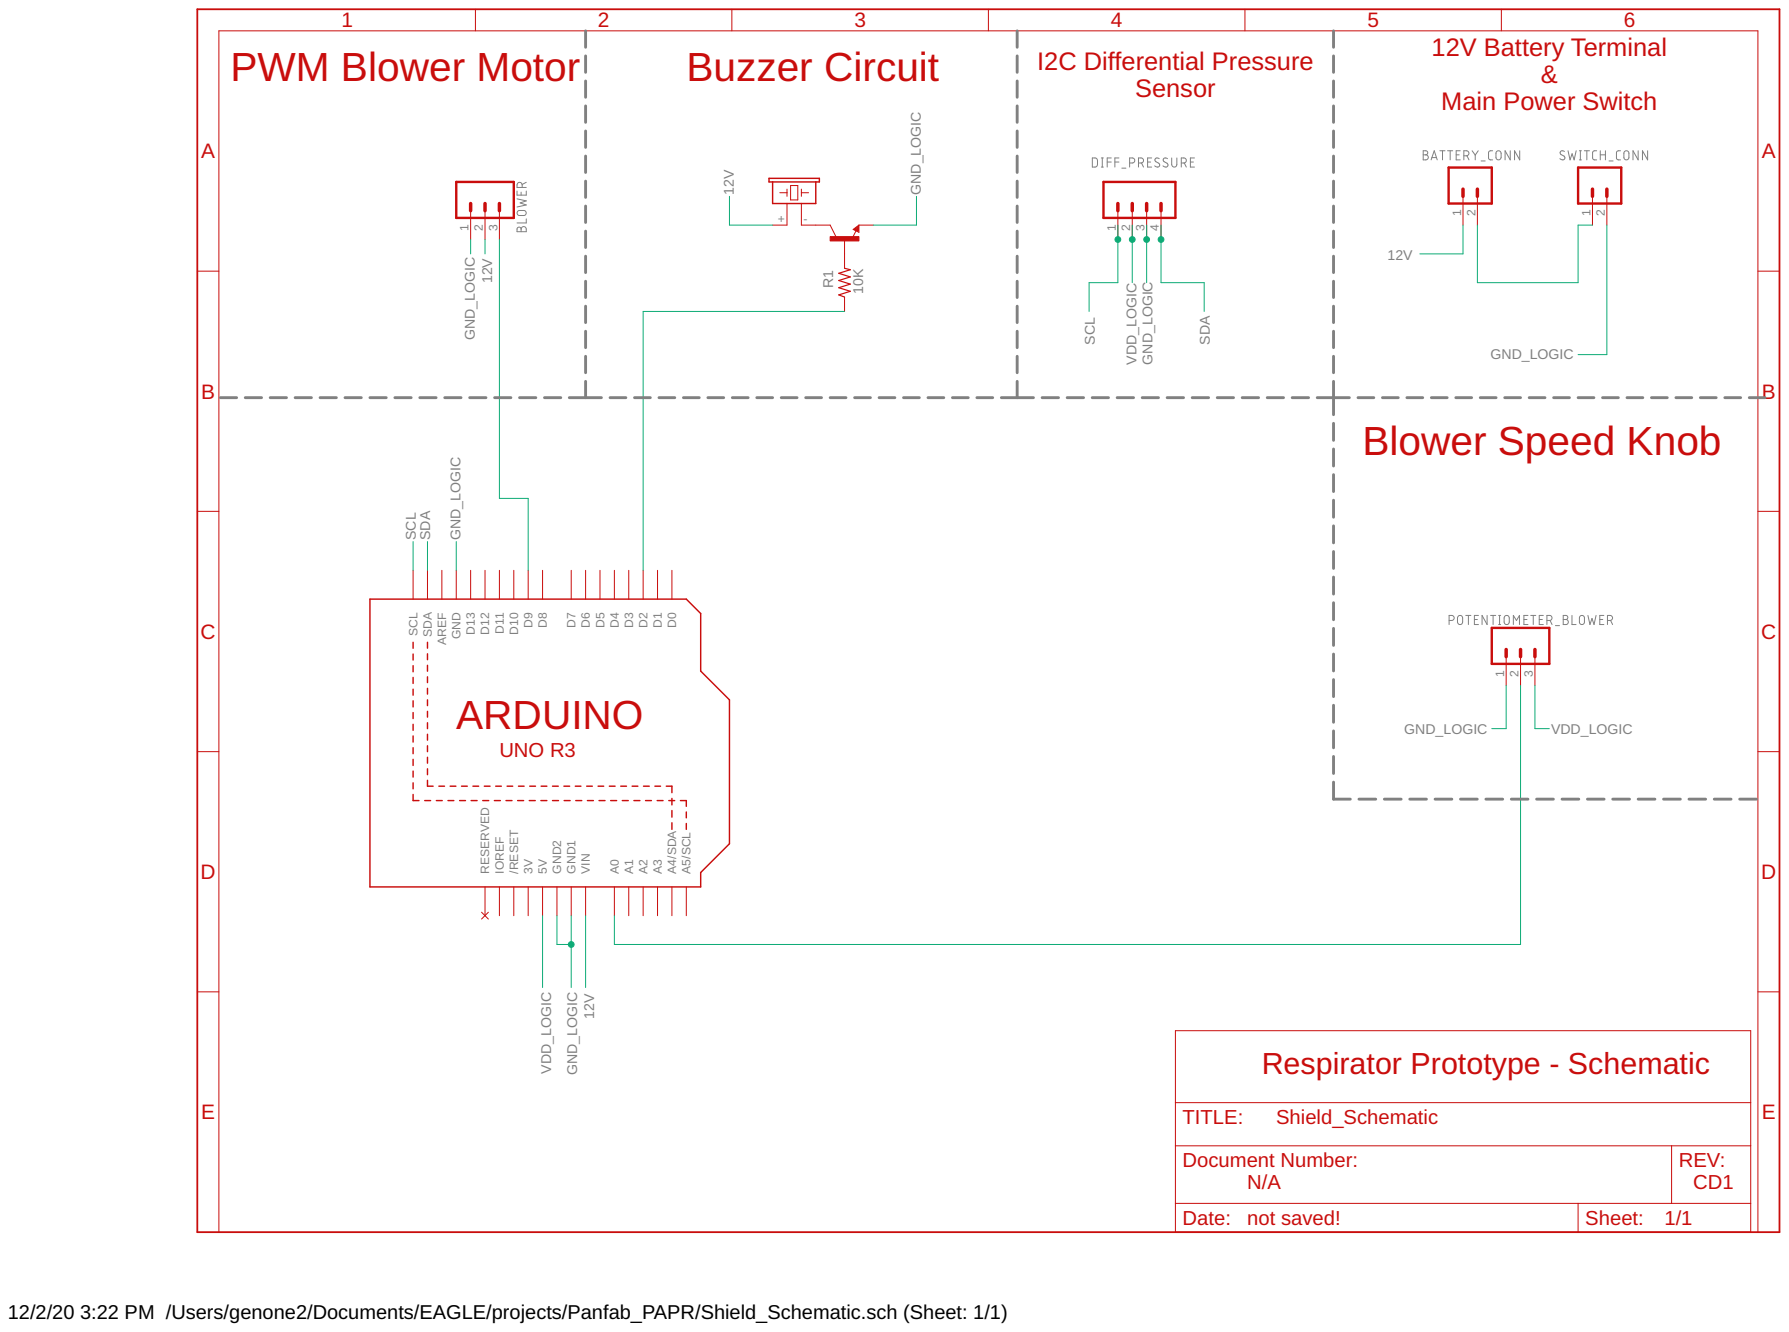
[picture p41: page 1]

Main Power Switch

Document Number: N/A | REV: CD1

Date: not saved! | Sheet: 1/1

12/2/20 3:22 PM /Users/genone2/Documents/EAGLE/projects/Panfab_PAPR/Shield_Schematic.sch (Sheet: 1/1)

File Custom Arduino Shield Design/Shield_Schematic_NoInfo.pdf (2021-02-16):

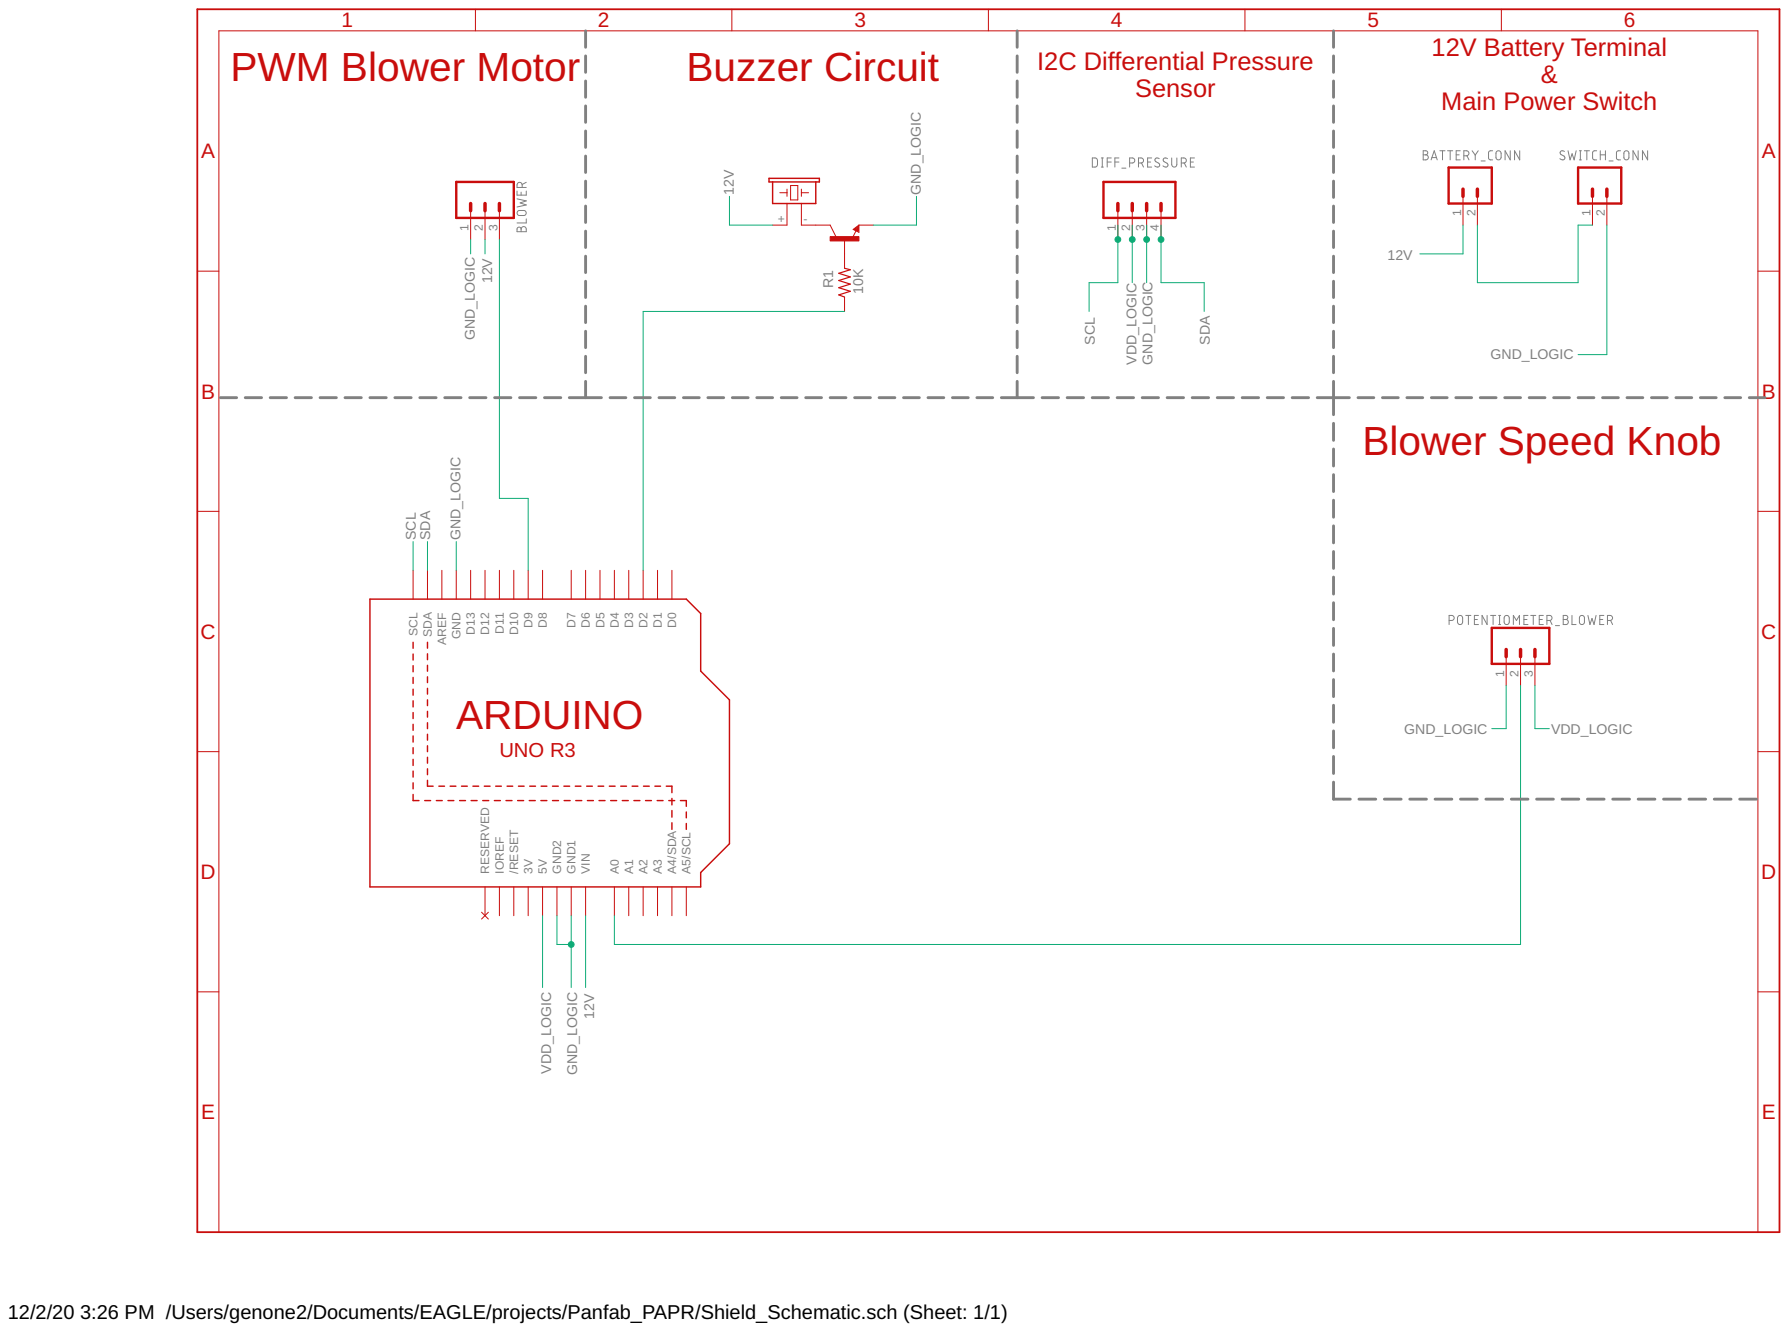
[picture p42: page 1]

Main Power Switch

12/2/20 3:26 PM /Users/genone2/Documents/EAGLE/projects/Panfab_PAPR/Shield_Schematic.sch (Sheet: 1/1)

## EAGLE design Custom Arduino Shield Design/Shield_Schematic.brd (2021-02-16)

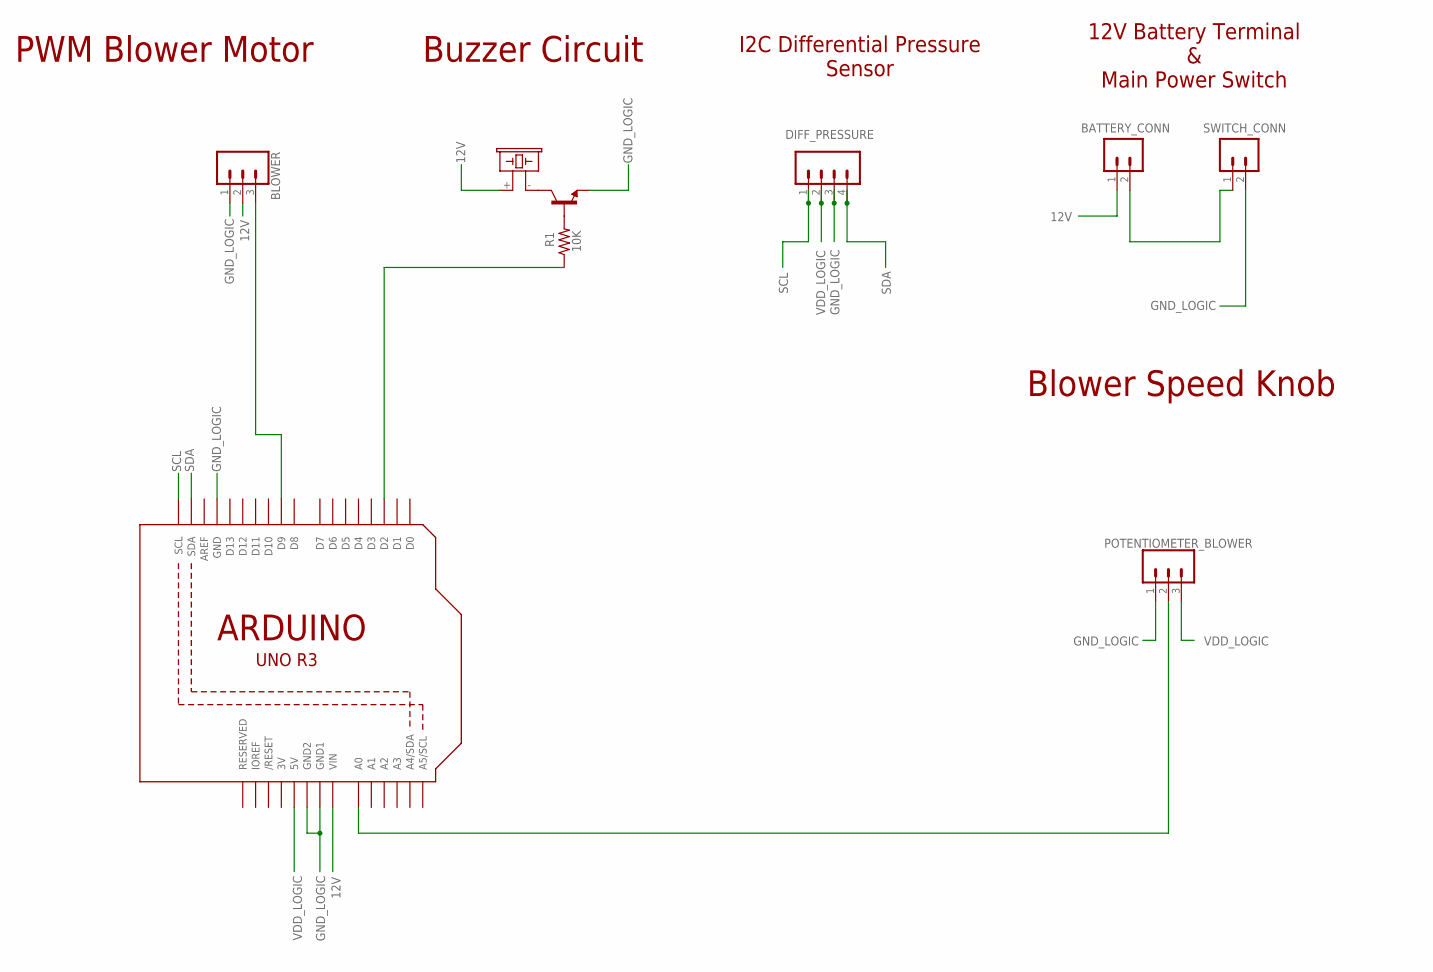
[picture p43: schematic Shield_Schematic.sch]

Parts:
BATTERY_CONN: CONN_02PTH4; 1X02_XTRA_BIG
BLOWER: CONN_03; 1X03
DIFF_PRESSURE: CONN_04; 1X04
POTENTIOMETER_BLOWER: CONN_03; 1X03
R1: 10K; P0817V
SG1: F/CM12P
SWITCH_CONN: CONN_02PTH4; 1X02_XTRA_BIG
T1: 2N5089; TO92
U1: ARDUINOR3-DIMENSION; ARDUINOR3

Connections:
3V: U1.3V
12V: BATTERY_CONN.1, BLOWER.2, SG1.+ (1), U1.VIN
GND_LOGIC: BLOWER.1, DIFF_PRESSURE.3, POTENTIOMETER_BLOWER.1, SWITCH_CONN.2, T1.3 (E), U1.GND, U1.GND1, U1.GND2
unnamed: POTENTIOMETER_BLOWER.2, U1.A0
unnamed: BLOWER.3, U1.D9
unnamed: R1.1, U1.D2
unnamed: R1.2, T1.2 (B)
unnamed: SG1.- (2), T1.1 (C)
unnamed: BATTERY_CONN.2, SWITCH_CONN.1
SCL: DIFF_PRESSURE.1, U1.SCL
SDA: DIFF_PRESSURE.4, U1.SDA
VDD_LOGIC: DIFF_PRESSURE.2, POTENTIOMETER_BLOWER.3, U1.5V

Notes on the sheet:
PWM Blower Motor
Buzzer Circuit
I2C Differential Pressure Sensor
12V Battery Terminal & Main Power Switch
Blower Speed Knob

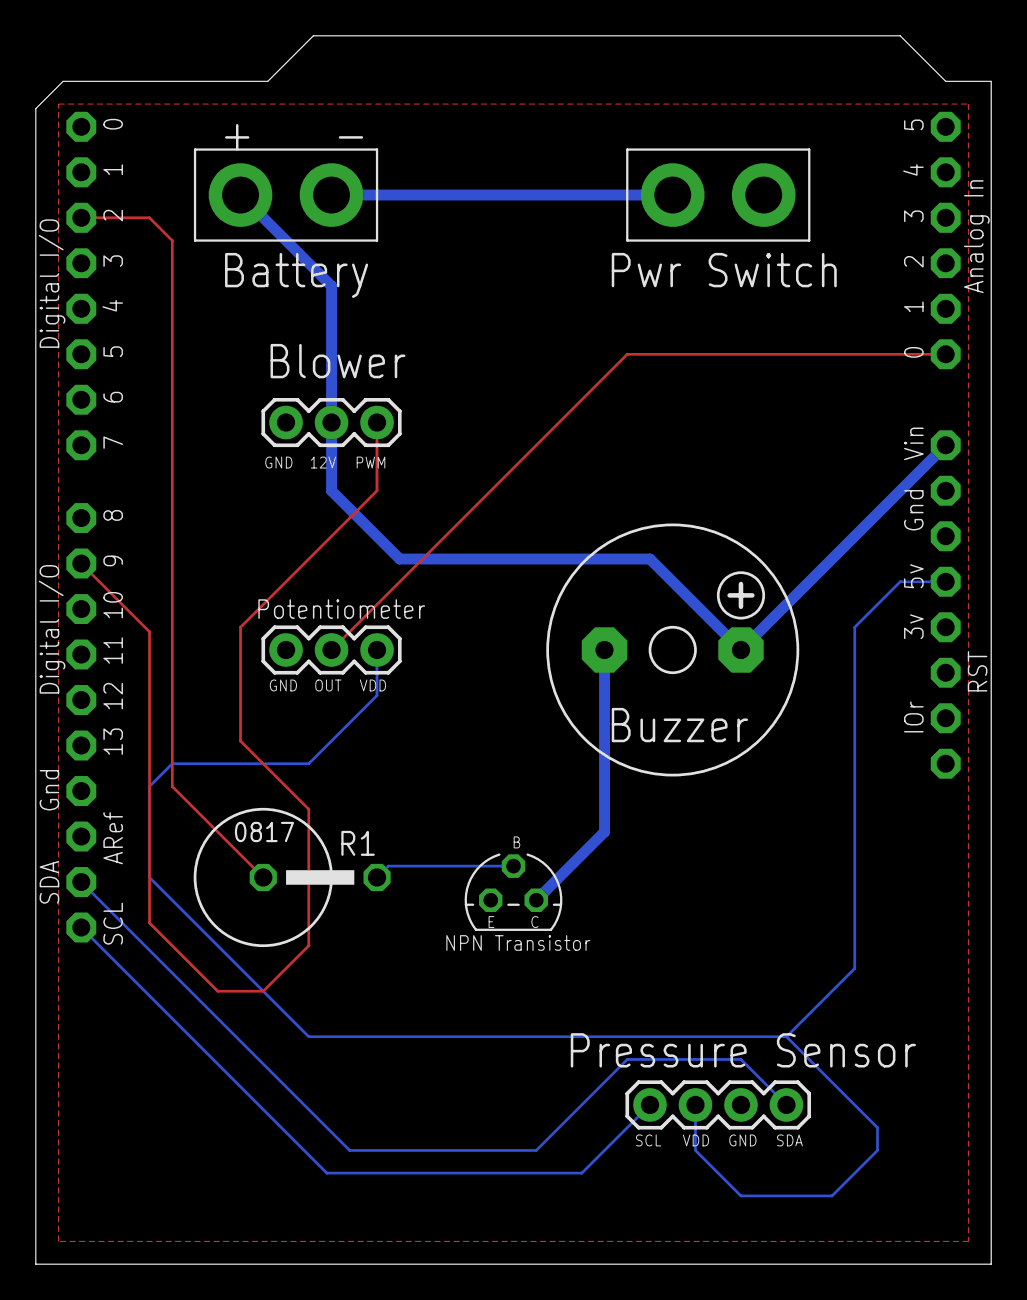
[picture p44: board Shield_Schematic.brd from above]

Board: 2 copper layers, 53.3 x 68.6 mm, 9 parts (0 on the bottom side), 11 nets.

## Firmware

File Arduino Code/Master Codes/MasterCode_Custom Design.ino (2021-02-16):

 #include <Wire.h>

#include <SoftPWM.h>

#include <sdpsensor.h>

SDP8XXSensor sdp;

//Stores the minimum interval before activating the timer, in milliseconds
unsigned long MinAlarm = 10 * 1000; // * 60 seconds/min

//stores the amount of time since the last alarm-qualifying event
unsigned long startTime = 0;

//stores the current time regardless.
unsigned long currTime = 0;

//Stores the frequency of the buzzer tone in Hertz.
unsigned int BuzzTone = 500;



//Everything from here until the start of void setup is for PWM control
// Set up Arduino pin 9 as PWM channel 0:
// (For examples on how to set this see:
//  File > Examples > arduino-softpwm > SoftPWM_example )
SOFTPWM_DEFINE_CHANNEL(0, DDRB, PORTB, PORTB1);  //Arduino pin 9

/* Here you make an instance of desired channel counts you want
   with the default 256 PWM levels (0 ~ 255). */
SOFTPWM_DEFINE_OBJECT(1);

/* If you want to use the SoftPWM object outside where it's defined,
   add the following line to the file. */
SOFTPWM_DEFINE_EXTERN_OBJECT(1);

// set analog input pin
int analogInputPin = A0;
int digitalOutputPin = 2; 

void setup() {
  //the part below is for the diff. pressure sensor, until the while statement
  Wire.begin();
  Serial.begin(9600);
  delay(1000); // let serial console settle
  do {
    int ret = sdp.init();
    if (ret == 0) {
      Serial.print("init(): success\n");
      break;
    } else {
      Serial.print("init(): failed, ret = ");
      Serial.println(ret);
      delay(1000);
    }
  } while(true);

  //the part below, until the beginning of void loop is for the PWM control
  // begin with 100hz pwm frequency
  Palatis::SoftPWM.begin(100);
}

void loop() {
  //the part below, until the 'delay(10)' statement is for the PWM control
  long inputVal = analogRead(analogInputPin);

  // CONVERSION:
  // - analogRead() returns a value from 0..1023
  // - SoftPWM takes values from 0..255
  // - blower reaches max speed at 90%
  // - probably want to have a minimum blower speed too: minPWM
  // So, convert inputVal range from 0..1023 to minPWM..230
  const long minPWM = 64; // set min to be 25% of 255
  const long maxPWM = 230; // set max to be 90% of 255
  long PWMLevel = minPWM + (inputVal * (maxPWM-minPWM)) / (1023);

  currTime = millis();

  // set pin 9 (pwm channel 0) to new PWM level
  Palatis::SoftPWM.set(0, PWMLevel);
  Serial.println(PWMLevel); // debugging

  delay(10); // no need to respond to user input faster than ~100Hz

  //the part below, until the end is for the diff. pressure sensor
  int ret = sdp.readSample();
  if (ret == 0) {
    Serial.print("Differential pressure: ");
    Serial.print(sdp.getDifferentialPressure());
    Serial.print("Pa | ");

    Serial.print("Temp: ");
    Serial.print(sdp.getTemperature());
    Serial.print("C\n");
    if (sdp.getDifferentialPressure()<205) // this is for the low flow alarm
    {

      Serial.print("Low Alarm Activated: ");
      Serial.print((currTime - startTime)/1000);
      Serial.println(" sec.");
      if((currTime-startTime) >= MinAlarm)
      {
    tone(digitalOutputPin,BuzzTone);
      }
    }
    else
    {
      startTime = currTime;
    noTone(digitalOutputPin);
    }  
  }
  else {
    Serial.print("Error in readSample(), ret = ");
    Serial.println(ret);
  }
  //delay(10);
}

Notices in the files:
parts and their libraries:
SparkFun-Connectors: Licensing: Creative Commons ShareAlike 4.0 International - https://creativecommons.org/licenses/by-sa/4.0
